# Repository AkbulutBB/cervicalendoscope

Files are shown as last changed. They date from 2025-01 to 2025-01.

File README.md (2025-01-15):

Open Source Cervical Surgery Model

First, you print the silicone molds for the skin, spinal cord and the gasket for the lid. I suggest you create many molds for the cord, as it takes very little silicone to fill, and easier to do in big batches. Then you move on to the next step:

How to handle silicone: https://formlabs.com/asia/blog/how-to-make-silicone-molds/
TL;DR: You need a well ventilated area, some vinyl gloves, silicone release spray. After mixing the RTV Shore 5 silicone in quantities specified by the producer, you just pour into the mold. Wait 24 hours.

Then you need to print the dark chamber. I suggest using PETG for all the prints, as it's durable. Silicone molds can be out of PLA.

I suggest fixing the dark chamber to a big plastic tub, or atleast something you can hold on to easily. This way when the resident is using kerrison, whole assembly doesn't come with it. Alternatively you could fix the tub to a table using some belts.

Then out of white PETG, you should print the cervical model and remove the tree supports with pliers. Then you can put in the spinal cord into it, I found it easier to skewer the cord with a kirschner wire, and pull it through the spinal canal. Then using some forceps (a jeweler's kit works fine) you put the roots into their appropriate foramina.

After that is done, (I suggest you do this in batches again), wet your model with water then using expanding polyurethane spray, place the nozzle into the disc space and fill it up. After you see the foam coming out of the interlaminar line, move on to the next level. In the end, remove the excess foam from the lamina and under the transverse foramen with your gloves. This will make the later cleanup process easier. 

After 24 hours of curing, the foam is a solid mass, you can remove it from under the body, so it can slide into the dark chamber and also, remove it from over the lamina, so they are visible. You'll need a snap knife for this or a curved carving knife (like a mushroom knife). Alternatively, you could leave it in place, and ask the resident to dilate/disect the way into the surgical space, which is probably a more advanced way of doing this. 

Finally, you place the model into the dark chamber, lock the door with some M3 screws and nuts. And the model is ready. You don't need the silicone gasket at the door if you are not going to work completely underwater, due to budget concerns, the endoscope we used took water into its lens when working completely underwater and just dripped water into the field to prevent PETG from heating up and melting. 

Licence:


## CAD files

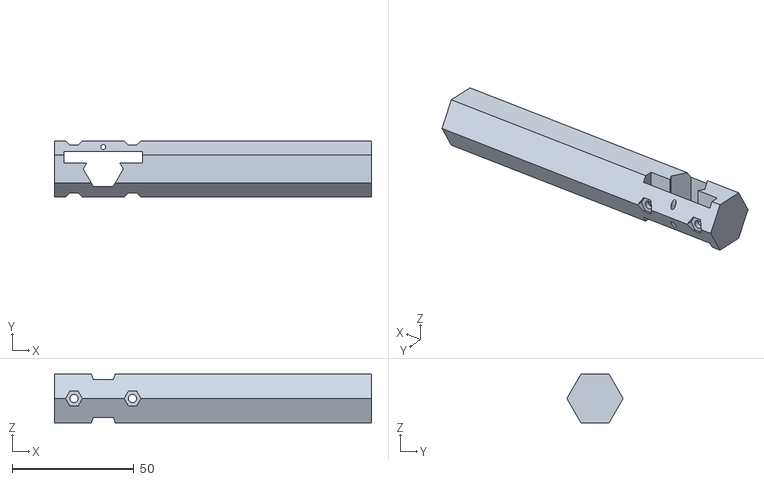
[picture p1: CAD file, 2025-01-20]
SimpleUBEHandle.stl
130.0 x 23.1 x 20.0

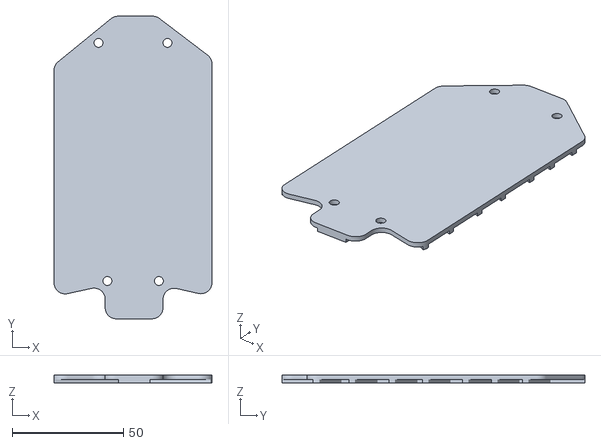
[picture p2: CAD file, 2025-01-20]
CordMoldCover.stl
71.0 x 136.0 x 3.50

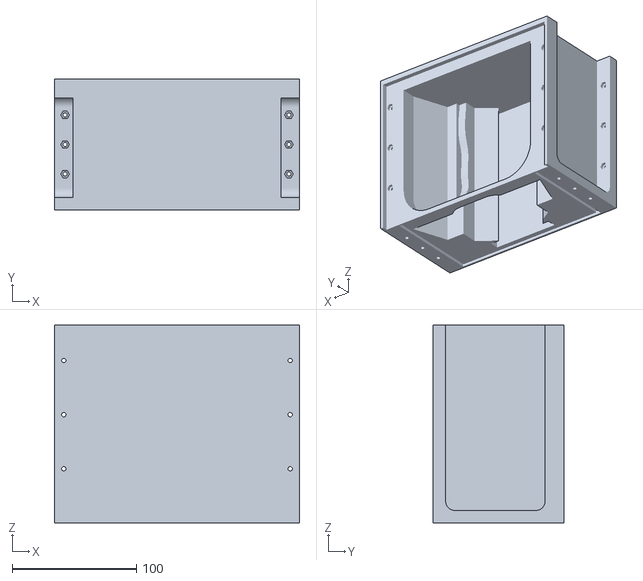
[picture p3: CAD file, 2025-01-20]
CervicalEndoBox (1) (1).stl
197.0 x 105.0 x 159.0

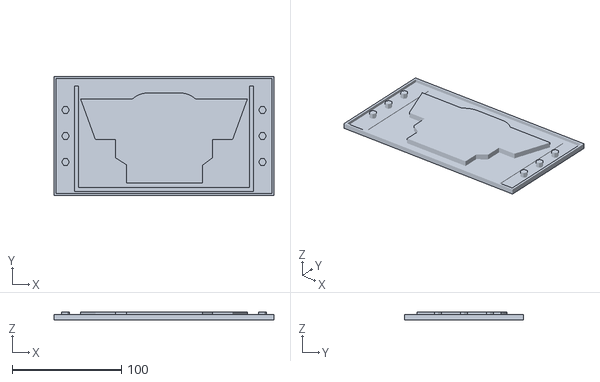
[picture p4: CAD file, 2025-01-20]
GasketMold.stl
201.0 x 109.0 x 7.00

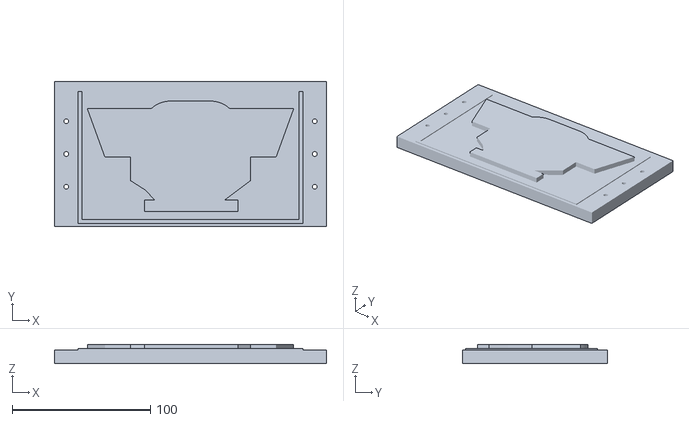
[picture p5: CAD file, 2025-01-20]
CervicalEndoscopeLid.stl
197.0 x 105.0 x 14.0

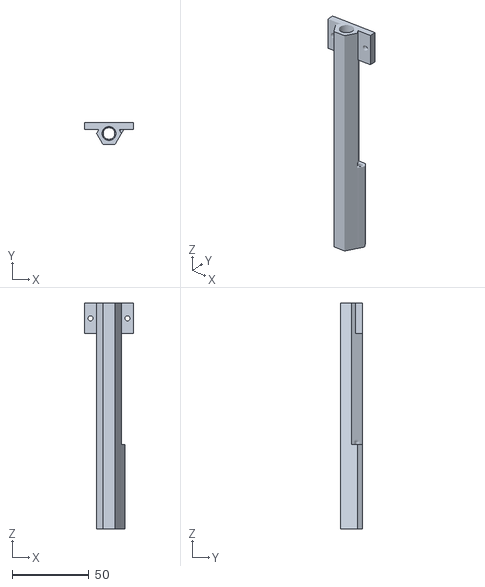
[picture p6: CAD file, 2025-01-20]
SimpleUBE.stl
31.8 x 14.0 x 147.0

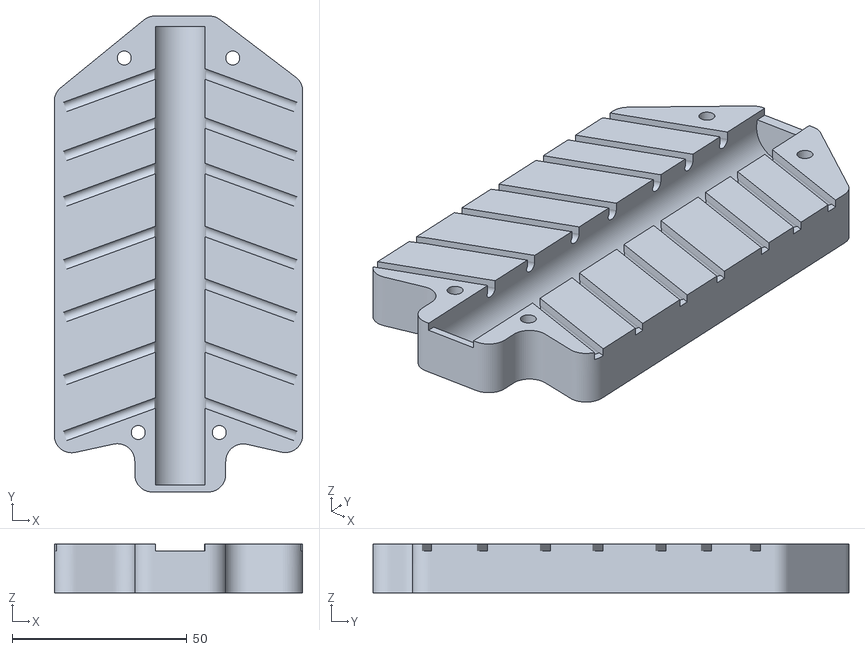
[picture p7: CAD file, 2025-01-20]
CordMold.stl
71.0 x 136.0 x 14.0

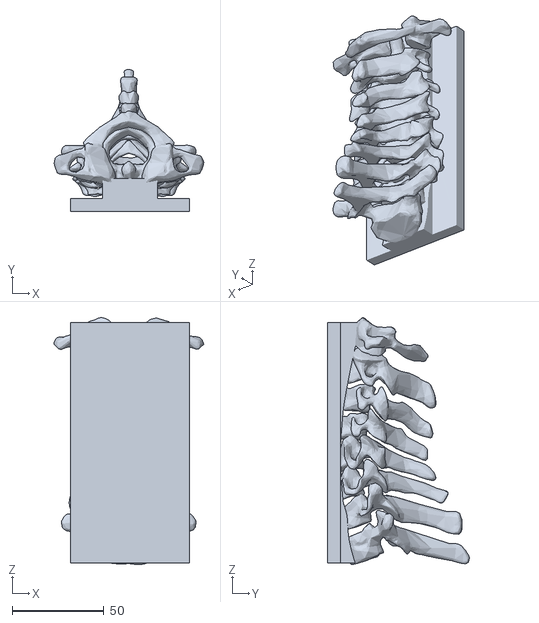
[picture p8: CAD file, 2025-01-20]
C1T1Fixed.stl
81.6 x 77.2 x 134.7

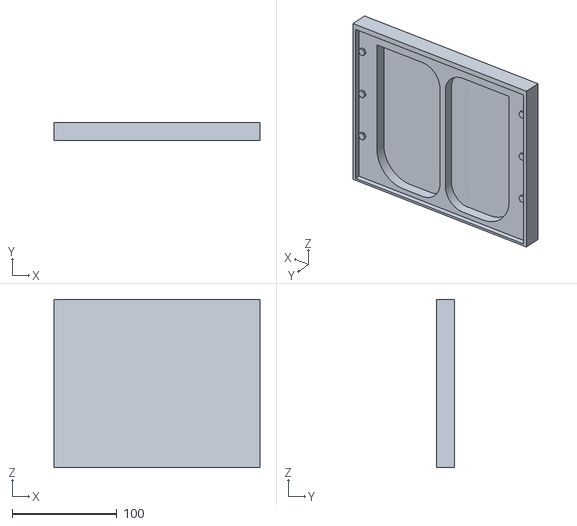
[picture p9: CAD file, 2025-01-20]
SkinMOld.stl
197.0 x 17.0 x 161.0
